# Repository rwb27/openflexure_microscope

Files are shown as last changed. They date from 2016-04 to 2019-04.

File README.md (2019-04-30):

# This repository has moved!
Active development continues on [GitLab.com](https://gitlab.com/openflexure/openflexure-microscope/) where you can find not only the up-to-date microscope designs, but also software and lots of other fun goodies.

# OpenFlexure Microscope
The OpenFlexure Microscope is a  3D printable microscope, including a precise mechanical stage to move the sample and focus the optics.  There are many different options for the optics, ranging from a webcam lens to a 100x, oil immersion objective.

An OpenFlexure Microscope in an incubator (courtesy Stephanie Reichelt and Dario Bressan at CRUK, Cambridge)

The trick of making a microscope out of a webcam has been around for a little while, and produces good results.  However, getting a nice mechanical stage to focus the microscope and move around on the sample is tricky.  This project is a 3D printable design that enables very fine (sub-micron) mechanical positioning of the sample and the lens, with surprisingly good mechanical stability.  It's discussed in various [media articles](https://github.com/rwb27/openflexure_microscope/wiki/Media-Articles) and a [paper in Review of Scientific Instruments](http://dx.doi.org/10.1063/1.4941068) (open access).

## Come join us!
Most of the development of this design has been done as part of various [research projects](http://www.bath.ac.uk/physics/contacts/academics/richard-bowman/index.html) - if you would like to join our research group at Bath, and you have funding or are interested in applying for it, do get in touch.  Check the University of Bath jobs site, or findaphd.com, to see if we are currently advertising any vacancies.  The team is bigger than Bath, though, and there are contibutors in Cambridge, Dar es Salaam, and beyond.

## Kits and License
This project is open-source and is released under the CERN open hardware license.  We are working on bring able to sell kits, and will update here once we have a good way of doing it,

## Printing it yourself
To build the microscope, go to [version 5.20 release](https://github.com/rwb27/openflexure_microscope/releases/tag/v5.20.0-b) and download the STL files and instructions.  Don't just print everything from the STL folder,
as there are a number of different configurations possible.  The [assembly instructions](http://rwb27.github.io/openflexure_microscope/docs/) contain instructions on what parts to print and how to build it.

If you've built one, let us know - add yourself to the [wiki page of builds](https://github.com/rwb27/openflexure_microscope/wiki/Assembly-Logs) or submit a [build report issue](https://github.com/rwb27/openflexure_microscope/issues/new?labels=build%20report).  This is a really helpful thing to do even if you don't suggest improvements or flag up problems.

## Instructions
The editable instructions are MarkDown format, in the [docs folder](./docs/), and [they can be viewed on github pages](http://rwb27.github.io/openflexure_microscope/docs/).

## Get Involved!
This project is open so that anyone can get involved, and you don't have to learn OpenSCAD to help (although that would be great).  Ways you can contribute include:

* Get involved in [discussions on gitter](https://gitter.im/OpenFlexure-Microscope/Lobby) 
* Share your microscope images (of both microscopes and what you've seen with them) in the [gallery](http://rwb27.github.io/openflexure_microscope/gallery/)
* [Raise an issue](https://github.com/rwb27/openflexure_microscope/issues) if you spot something that's wrong, or something that could be improved.  This includes the instructions/documentation.
* Suggest better text or images for the instructions.
* Improve the design of parts - even if you don't use OpenSCAD, STL files or descriptions of changes are helpful.
* Fork it, and make pull requests - again, documentation improvements are every bit as useful as revised OpenSCAD files.

Things in need of attention are currently described in [issues](https://github.com/rwb27/openflexure_microscope/issues) so have a look there if you'd like to work on something but aren't sure what.

## Related Repositories
Most of the Openflexure Microscope stuff lives on GitHub, under [my account](https://github.com/rwb27/).  Particularly useful ones are:
* The ["sangaboard" motor controller](https://github.com/rwb27/openflexure_nano_motor_controller/) based on an Arduino Nano + Darlington Pair ICs, developed collaboratively with [STICLab](http://www.sticlab.co.tz)
* The ["fergboard" motor controller](https://github.com/fr293/motor_board) by Fergus Riche
* An as-yet-quite-basic set of scripts that should become the [microscope software](https://github.com/rwb27/openflexure_microscope_software/)
* The higher precision, smaller range [block stage](https://github.com/rwb27/openflexure_block_stage)
* Some [characterisation scripts for analysing images of the USAF resolution test target](https://github.com/rwb27/usaf_analysis/)

## Compiling from source
If you want to print the current development version, you can compile the STL from the OpenSCAD files - but please still consult the documentation for quantities and tips on print settings, etc.  You can use GNU Make to generate all the STL files (just run ``make all`` in the root directory of the repository).  More instructions, including hints for Windows users, are available in [COMPILE.md](https://github.com/rwb27/openflexure_microscope/blob/master/COMPILE.md).

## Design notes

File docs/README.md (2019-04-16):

# The OpenFlexure Microscope: Assembly Instructions
The OpenFlexure Microscope is a 3D printable microscope, with a very precise mechanical translation stage.  It can be fitted with basic webcam-based optics, or more expensive optics based on a traditional microscope objective for higher image quality.  It can also be motorised.  These instructions will take you through how to assemble the microscope optical and mechanical parts.

## Printing the parts
Before we start, a note on printing - there are many possible versions of the microscope, so don't just print everything in the folder of STL files.  Currently, there's a readme document in the ``builds`` folder explaining how to select your versions.  Please do consult it before printing.  Also note that the parts are designed to print without support material on most RepRap type printers.  If you use support material, the parts will be difficult to clean up, and may well be damaged in the process - particularly the delicate main body.

## Contents
Assembly is broken up into several steps:
* [Obtaining non-printed parts](./0_bill_of_materials.md)
* [Printing parts](./0_printing.md)
* [Assembling the actuators](./1_actuator_assembly.md) deals with the mechanism for moving the stage.
* The optics module comes next, either the [basic optics module](./2a_basic_optics_module.md) or the [high resolution optics module](./2b_high_resolution_optics_module.md) depending on your needs.
* [Illumination](./3_illumination.md) covers attaching the condenser.
* [Sample clips and wiring](./4_clips_and_wiring.md) completes the microscope.
* [Motors](./5_motors.md) can be added for automatic control.

Happy building!

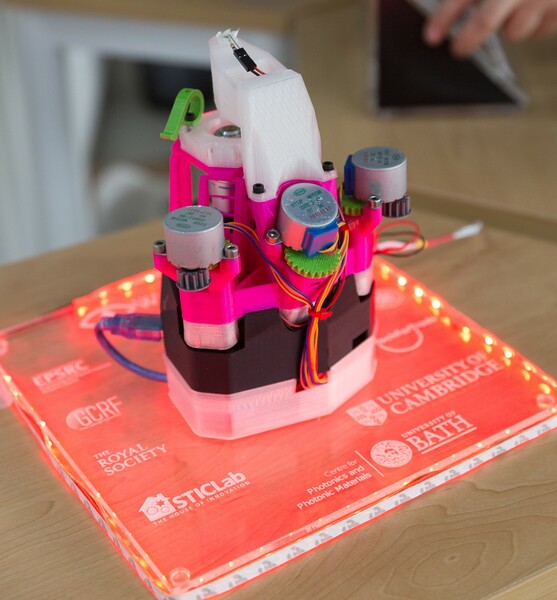
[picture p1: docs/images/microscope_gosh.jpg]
An assembled OpenFlexure Microscope, courtesy of GOSH 2018


## About the microscope
The OpenFlexure microscope is a customisable optical microscope, using either very cheap webcam optics or lab quality, RMS threaded microscope objectives.  It uses an inverted geometry, and has a high quality mechanical stage which can be motorised using low cost geared stepper motors.

The original paper describing this work is available open-access from [Review of Scientific Instruments](http://dx.doi.org/10.1063/1.4941068) and you can read various [media articles](https://github.com/rwb27/openflexure_microscope/wiki/Media-Articles) about it for a more user-friendly introduction.

Optomechanics is a crucial part of any microscope; when working at high magnification, it is absolutely crucial to keep the sample steady and to be able to bring it into focus precisely.  Accurate motion control is extremely difficult using printed mechanical parts, as good linear motion typically requires tight tolerances and a smooth surface finish.  This design for a 3D printed microscope stage uses plastic flexures, meaning its motion is free from friction and vibration.  It achieves steps well below 100nm when driven with miniature stepper motors, and is stable to within a few microns over several days.

This design aims to minimise both the amount of post-print assembly required, and the number of non-printed parts required - partly to make it as easy as possible to print, and partly to maximise stability; most of the microscope (including all the parts with flexures) prints as a single piece.  The majority of the expense is in the Raspberry Pi and its camera module; the design requires only around 200g of plastic and a few nuts, bolts and other parts.  The optics module (containing the camera and lens) can be easily swapped out or modified, for example to change the magnification/resolution by using a microscope objective, or adding a filter cube for fluorescence.

## Acknowledgements
This design has largely come out of academic research projects, and we would like to acknowledge financial support from:
* The [Engineering and Physical Sciences Research Council](http://epsrc.ukri.org/) (grants EP/P029426/1, EP/R013969/1)
* The Royal Society
* The Royal Commission for the Exhibition of 1851
* Queens' College, Cambridge

The lead developer started this project while at the University of Cambridge, and continues to work on it at the University of Bath, UK.

## Contributors
* Richard Bowman <r.w.bowman@bath.ac.uk> (University of Bath)
* Julian Stirling (University of Bath)
* Grace Anyelwisye Mwakajinga (STICLab)
* Valerian Sanga (STICLab)
* Qixing Meng (University of Bath)

This design is (c) the contributors, released under the CERN open hardware license.

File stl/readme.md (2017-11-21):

# OpenFlexure Microscope STL Files
tl;dr **don't print these files if you want a microscope!** You should either go to the [documentation](../docs/) or the automatically built files in [builds](../builds/) (see the readme there for details of how to pick the right files to print).  You can also clone the repository and build it yourself if you have ``make`` and ``openscad``.  Bear in mind that these STL files might not perfectly match the instructions, as they get improved faster than the photos can be re-taken!

This folder is for STL files that have been compiled outside of the usual build process.  It's possible I should have excluded these from the repo, as they are build products - but it's often handy to have them here.  I will probably get rid of this folder in the future.  *Please don't just print this folder* as it does not add up to a full microscope!

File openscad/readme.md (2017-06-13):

OpenFlexure Microscope: OpenSCAD Source
=======================================

This folder contains the source code that generates the STL files that you print to produce the microscope.  The relationship between the source files and the STL files is not yet 1:1, though I'm gradually working on that.  Most of the SCAD files produce a corresponding STL, but there are a few key support files that don't:

* ``microscope_parameters.scad`` defines most of the important variables (parameters) used in the design, for example the size of the microscope, whether or not it has motor lugs, etc. etc. - this is the file you are most likely to need to modify, for example to produce a microscope with particular settings.
* ``utilities.scad`` contains lots of handy functions I've coded along the way.  It's a slightly random assortment, but they are used in most of the other files and save a fair bit of typing.
* ``dovetail.scad`` defines the dovetail clips used to hold the optics module and the condenser.
* ``compact_nut_seat.scad`` defines the actuator column (the bit that holds the screw, nut and elastic band).  This is one of the most useful files for other projects - e.g. the OpenFlexure Block Stage uses it extensively.
* ``logo.scad`` is used to stamp the WaterScope logo on the microscope

Then for the main parts of the microscope:
* ``main_body.scad`` defines the main body.  This is by far the biggest file as you might expect.
* ``feet.scad`` produces the three front feet (two tilted and one untilted)
* ``gears.scad`` makes 3 gears for the actuators.
* ``illumination_and_rear_foot.scad`` produces the illumination column, which is combined with the back foot.  It's now in three pieces, for easier printing and to allow some adjustment of the condenser position.
* ``optics.scad`` defines, amongst other things, the optics module (the mount for the camera and objective).  This has a number of commented-out sections that must be uncommented depending on what you want to produce.  In particular, you must choose manually between an RMS objective and using a simpler lens.  You must also uncomment the correct line at the top of the file for the camera - the design will work with several camera modules defined in the ``cameras`` folder.
* ``sample_clip_2.scad`` produces clips to hold microscope slides onto the microscope stage.  This is now set to print two, and produces an STL file that is print-ready (i.e. the clips are on their side).
* ``sample_riser_2.scad`` makes a 10mm thick platform for a microscope slide.  You may need to use comments at the bottom of the file to print either the sample riser or the clip that holds the slide on.  A small spring is required to put the clip in the right place.
* ``small_gear.scad`` makes the gear you fit on a motor if you want to motorise the microscope.  NB it only makes one gear.

There are some that make tools too:
* ``actuator_assembly_tools.scad`` defines the tool for inserting elastic bands, and the tooll for pushing nuts into nut slots.  NB there is a new double-ended band tool defined at the bottom of the file, you'll need to use the comments to either produce this or the old-style one.
* ``tube_lens_tool.scad`` produces a ring of plastic, suitable for pushing the tube lens into its push-fit mount without damaging it.
* ``condenser_lens_tool.scad`` produces a ring of plastic, suitable for pushing the condenser lens into its push-fit mount without damaging it.
* ``lens_removal_tools.scad`` produces the tools needed to remove the lens from the Raspberry Pi camera module.  NB the lens removal tool is now superseded by the injection-moulded tool supplied by Raspberry Pi with each camera, but the board holder still helps to avoid damaging the flex.

Other files:
* ``baseplate.scad`` and ``baseplate_minimal.scad`` generate a baseplate, suitable for gluing onto some foam, if you want to mount the microscope in a box.  It's still work in progress...
* ``illustrations/`` contains various SCAD files that aim to create the illustrations needed for the instructions.  Very much work in progress, it's nowhere near finished.

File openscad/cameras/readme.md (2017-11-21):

# OpenFlexure Microscope: Camera Mounts

Curently, the OpenFlexure microscope will work with:
* Raspberry Pi camera module v2 (v1 is possible but deprecated, as it's discontinued)
* Logitech C270 webcam (you need to dissassemble it and remove the microphone)
* USB camera with standard M12 lens (WaterScope source these from China)

The way this is done is that ``optics.scad`` includes ``camera.scad``, which defines the important functions/modules for interfacing with the camera.  These are then used to make the optics module accordingly.  The variable ``camera`` (defined in ``microscope_parameters.scad`` or on the command line). Those functions are:

* ``camera_mount_height()``: a function that returns the height of the mount (above this height, we will make the optics module - this is the distance below the ground plane of the microscope body that the camera PCB will sit).
* ``camera_sensor_height()``: the distance above the PCB that the camera sensor sits - it's used in the optics module to calculate the position of the lens.
* ``camera_mount()``: a module that builds a mount for the camera.  If you print this on its own, it should create a flat(ish) structure, ``camera_mount_height()`` high, that fits onto the camera, with the sensor centred on the origin.

There are 3 options for the camera:
* picamera_2: mount for Raspberry Pi camera v2
* logitech_c270: for Logitech C270 webcam
* m12: this replaces the M12 lens holder on a USB camera.  It should work with most cameras that have an M12 lens held onto the board by two screws.

The ``picamera_2.scad`` file also defines the cover for the bottom of the camera PCB and the tools for removing the lens (see below).  There's no cover for the Logitech PCB, I often use a bit of extra-large heatshrink (it's thinner than a printed cover would be, which is helpful).

Previous versions of the microscope had push-fit mounts for the Pi camera v1 and v2, but it was very easy to break the delicate flex on the camera module when fitting these, so they are now removed.  See previous versions if you need those.

## Pi Camera v2 accessories
The extra files ``picamera_2_<thing>.scad`` generate the board gripper and lens gripper that can be used to remove the lens of the Raspberry Pi camera v2, and a little cover for the bottom of the PCB to protect it from shorts, etc.  The lens gripper is now obsolete as a much better, injection-moulded gripper is now supplied in the pi camera box.  The gripper for the PCB is still useful as it protects the flex cable from damage while you remove the lens.

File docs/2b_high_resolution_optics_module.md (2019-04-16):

# High resolution optics module
To get lab quality images from your microscope, you need to use more sophisticated optics than a webcam lens.  This optics module uses an RMS threaded microscope objective, with a tube length correction lens, to take very high quality images.

# Requirements
You will need the parts shown in the picture below:

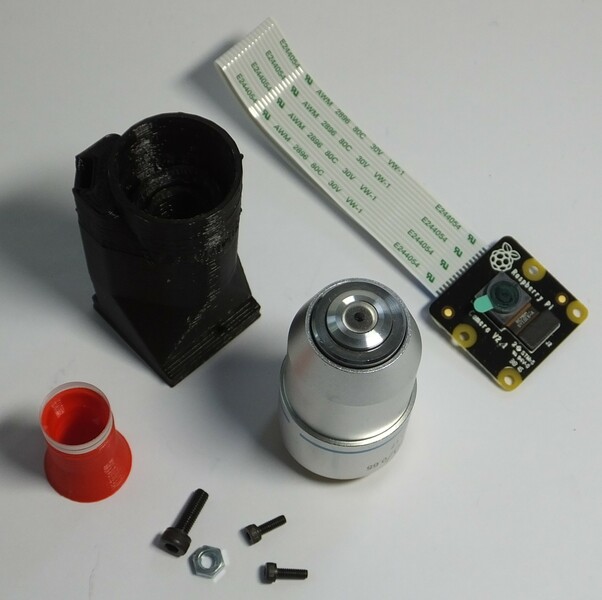
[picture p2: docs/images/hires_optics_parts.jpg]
Parts required for this step


## Parts
*   1 [RMS optics module casing](./parts/hires_optics_casing)
*   1 [Raspbery Pi camera module](./parts/electronics/raspberry_pi_camera.md)  (ideally v2, though v1 should also work)
*   1 [M3 steel nut](./parts/fixings/m3_steel_nut.md)
*   1 [M3x10mm cap head screw](./parts/m3x10mm_cap_head)
*   2 [M2x6mm cap head screws](./parts/m2x6mm_cap_head)
*   1 [12.7mm diameter, 50mm focal length achromatic lens](./parts/d13_f50_achromat)
*   1 RMS threaded microscope objective

## Tools
*   1 [Tube lens insertion tool](./parts/tube_lens_insertion_tool)
*   1 2.5mm hex key
*   1 1.5mm hex key
*   1 scalpel or craft knife (optional)
*   1 [Tool for removing the lens](./parts/camera_lens_removal_tools)

# Assembly Instructions
## Step 1
First, get the necessary tools and parts: the optics module plastic part, the Raspberry Pi camera module, the tools for removing the camera lens, two M2 screws to secure the camera, the tube lens, and the objective.  Depending on print quality, you might also need a sharp craft knife.
 
NB the lens removal tools, board gripper, and optics module are all specific to the camera you're using.  This version of the instructions is for version 2 of the camera board, version 1 of the Rasbperry Pi camera module will also work, but you will need to remove the lens with pliers or tweezers instead.  Version 2 of the camera module ships with a lens removal tool included, which is a white disc of plastic with a hole in the centre.  This is better than the printed lens removal tool, if it's available.

## Step 2
Before assembling the parts into the holder, make sure it's free from dust by blowing some air through it, and check there are no strings of plastic in the central hole through the mount - an example with strings of plastic is shown in the picture.  Use a craft knife to remove these strings, and blow out any debris that remains inside the optics module.

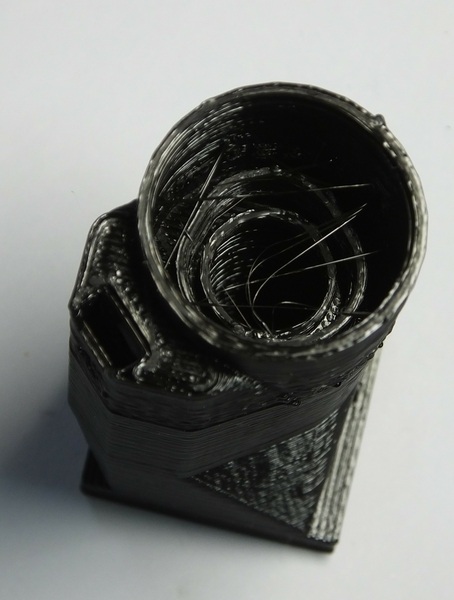
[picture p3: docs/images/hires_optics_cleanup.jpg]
Strings of plastic in the optics module


## Step 3
Slide the M3 nut into the plastic holder, and screw the M3 screw into it as shown.  This will mount the optics module into the microscope.

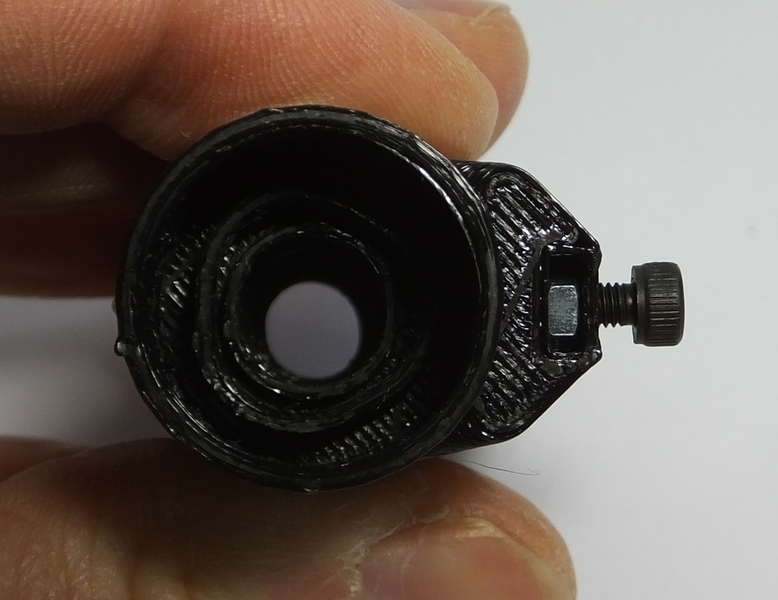
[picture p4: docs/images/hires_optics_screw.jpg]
Adding the mounting screw and nut


## Step 4
Next, put the lens into the push-fit holder.  Start by placing the tube lens insertion tool on a table, with the larger end down.  Then, put the lens on the tool (shown in red below), with the more convex side facing down.  Next, carefully line up the optics module casing with the lens, and push it down on top of the lens.  This might take a little force, I use the heel of my hand.  The glass lens is harder than the plastic so is unlikely to crack, but try to avoid too much sideways motion, as this can scratch the surface of the lens.

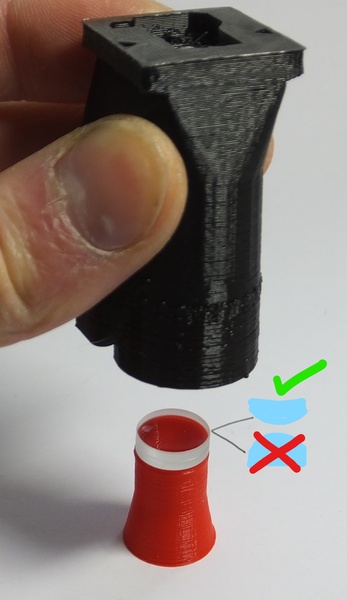
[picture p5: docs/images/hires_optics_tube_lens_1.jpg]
The lens ready to be inserted

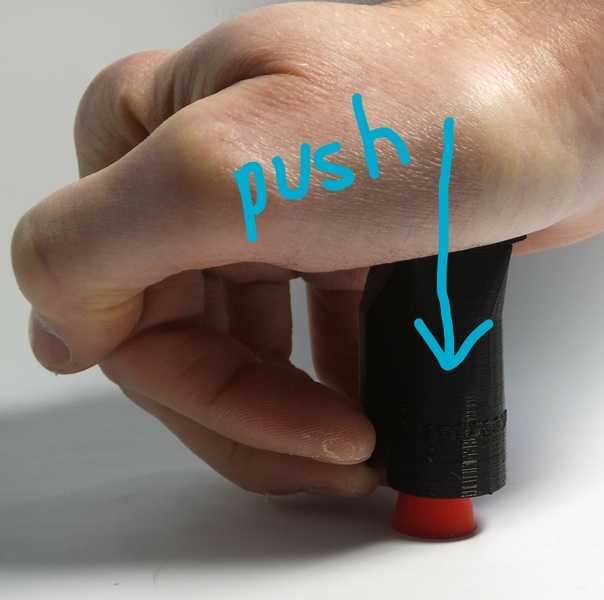
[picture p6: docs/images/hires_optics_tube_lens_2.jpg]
Inserting the lens

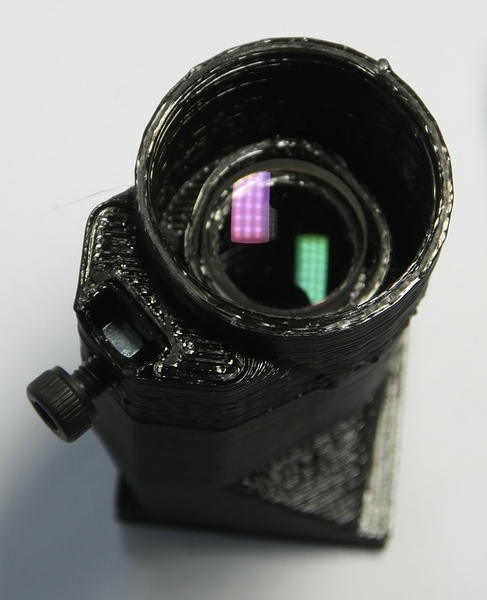
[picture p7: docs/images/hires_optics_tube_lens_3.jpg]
The tube lens, fitted into the optics module


## Step 5
Screw the objective into the plastic casing.  The printed thread is not hugely strong, and may not have printed very precisely - the means it might be a little loose or a little tight, and you need to be very careful to screw the objective in straight in order to avoid cross-threading.

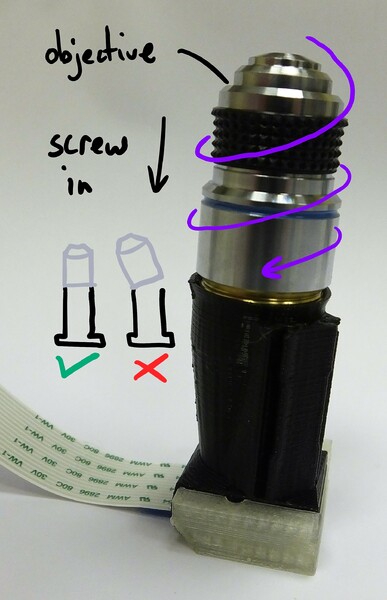
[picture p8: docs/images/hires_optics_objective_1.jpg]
Screw the objective in to the mount - be careful to keep it straight!

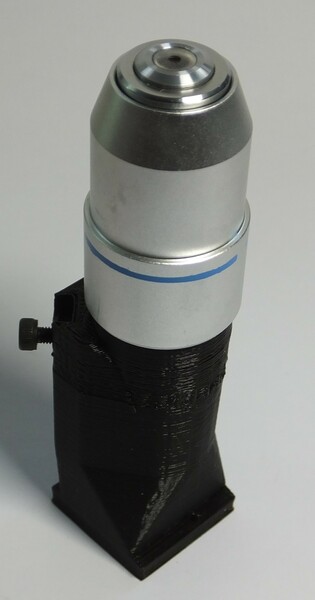
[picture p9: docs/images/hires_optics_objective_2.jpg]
The objective, in place in the optics module


## Step 6
We need to remove the lens from the camera.  To do this, you need the two plastic tools (the board gripper and the lens remover) as well as the camera module.  It's best to make sure you have completed the steps up to this point before removing the lens, to minimise the amount of time the sensor is exposed to air and dust.

> **WARNING!** The camera board is static sensitive.  Take the usual anti-static precautions (ideally use an anti-static wristband connected to ground, but at the very least make sure you touch an earthed object, such as a metal pipe, before working on the camera module.

## Step 7
Remove the protective film from the camera lens.

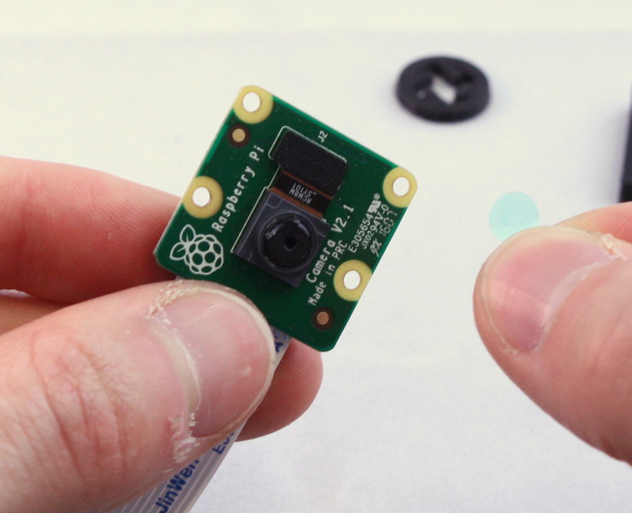
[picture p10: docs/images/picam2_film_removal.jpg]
Removing the protective film from the lens


## Step 8
There is a small ribbon cable connecting the camera to the PCB that is very easy to break.  There is a square plastic jig that fits over the camera and PCB (the "camera board gripper"), which stops the camera twisting and damaging the ribbon cable.  Fit this over the camera as shown.  Note that the part for v2 of the camera board will sort-of fit v1, but you need to be a little more careful as it's not a perfect fit.

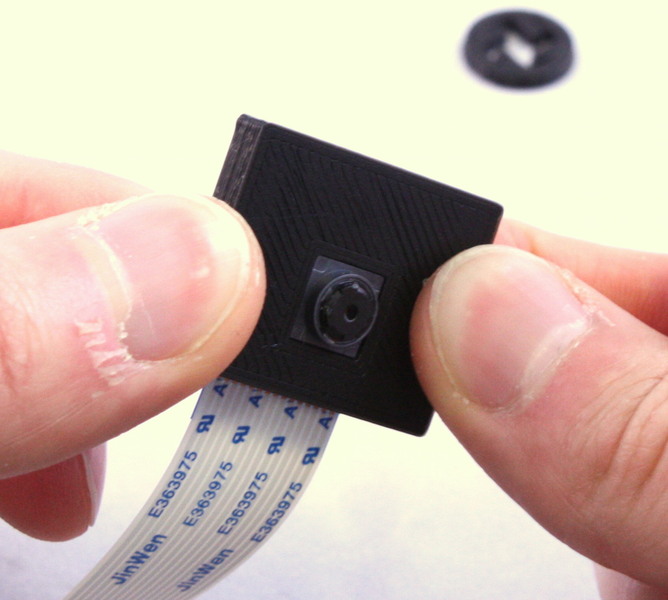
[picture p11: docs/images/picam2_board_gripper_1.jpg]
The board gripper

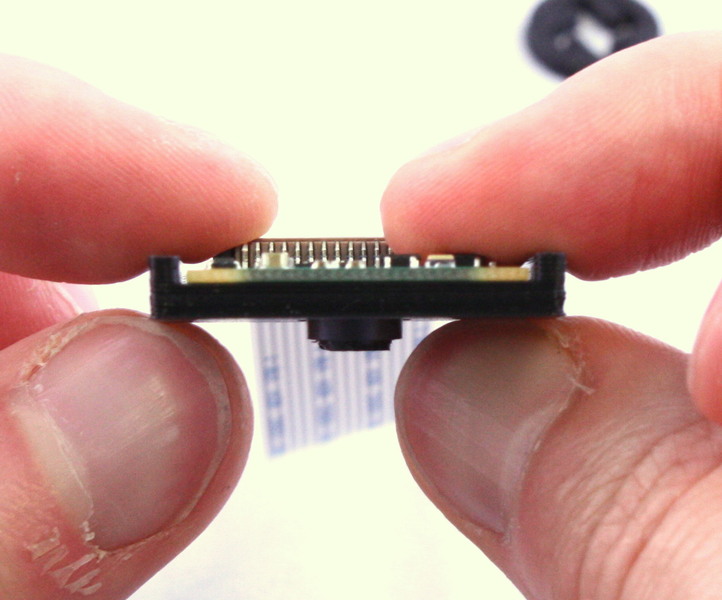
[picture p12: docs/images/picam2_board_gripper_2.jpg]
Gripping the camera to prevent damage to the ribbon cable


## Step 9
Next, unscrew the lens from the camera module.  Use the plastic tool to grip the lens module.  This is a small circular part with four prongs that fits over the lens of the camera board (version 2 only) as shown.  To remove the lens, push the removal tool onto the lens (just the top part, with the little plastic flanges) and turn anticlockwise to remove it.
 
The printed tool only works if the prongs are pointing anticlockwise, so make sure it's the right way round.  The plastic tool supplied with the camera module is better, and only fits one way up.  It's important to use the board gripper to hold the camera chip in place and prevent damage to the delicate ribbon cable.  After you've removed the lens, check that the little black (or orange) ribbon cable connecting the camera module to the PCB is still connected - pop it back in by pushing it with a finger if needed.

Once you've removed the lens, be sure to place the camera face down on the desk, or put a piece of tape over the square black lens holder; this will help stop dust settling on the sensor, which is extremely hard to clean.

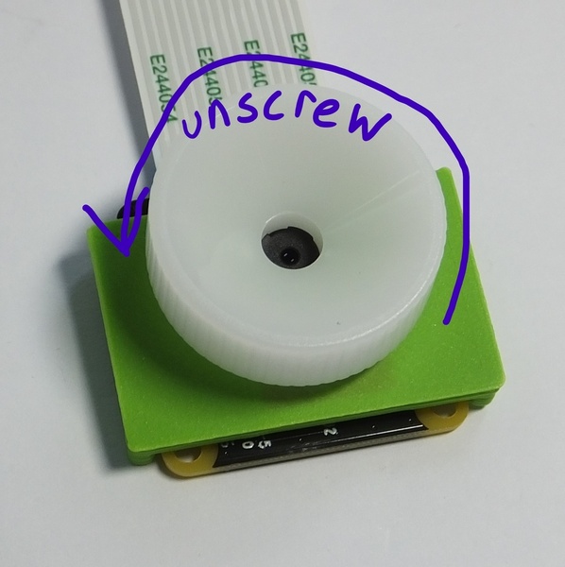
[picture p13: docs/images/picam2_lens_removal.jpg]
Lens removal


## Step 10
Fit the camera module on to the bottom of the plastic housing, and secure it in place with the two M2 screws.

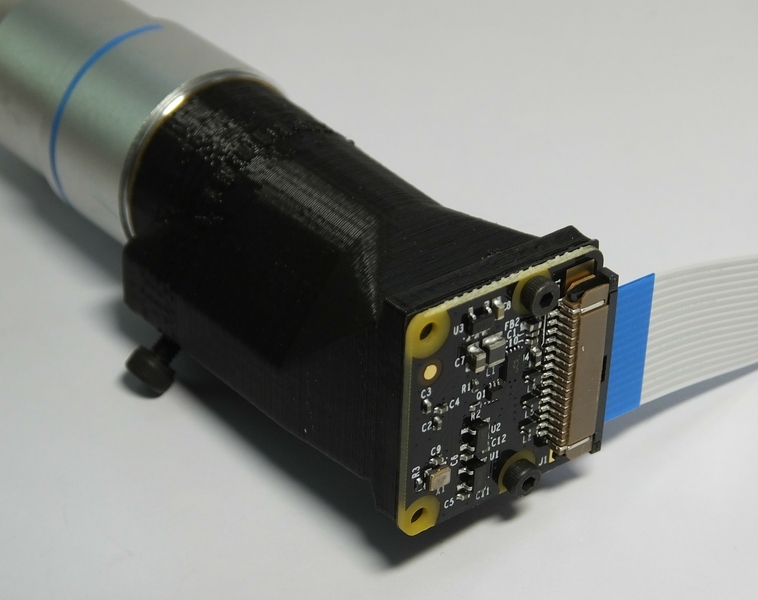
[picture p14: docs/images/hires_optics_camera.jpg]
The camera, held in place by two M2 screws


## Step 11
Well done - you have assembled the optics module.

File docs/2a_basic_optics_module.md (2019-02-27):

# Basic optics module
The simplest option for the microscope optics is to use a webcam lens.  This is an old photographers' trick, where a wide angle lens is turned backwards and used as a macro lens, so the side that would have pointed at the camera sensor now points at the sample.  Because webcams have very small pixels, using a webcam in reverse makes quite a good microscope objective.  This version of the optics module turns the Raspberry Pi camera into a microscope with a field of view about 400um across and a resolution of around 2um.

# Requirements
You will need the parts shown in the picture below:

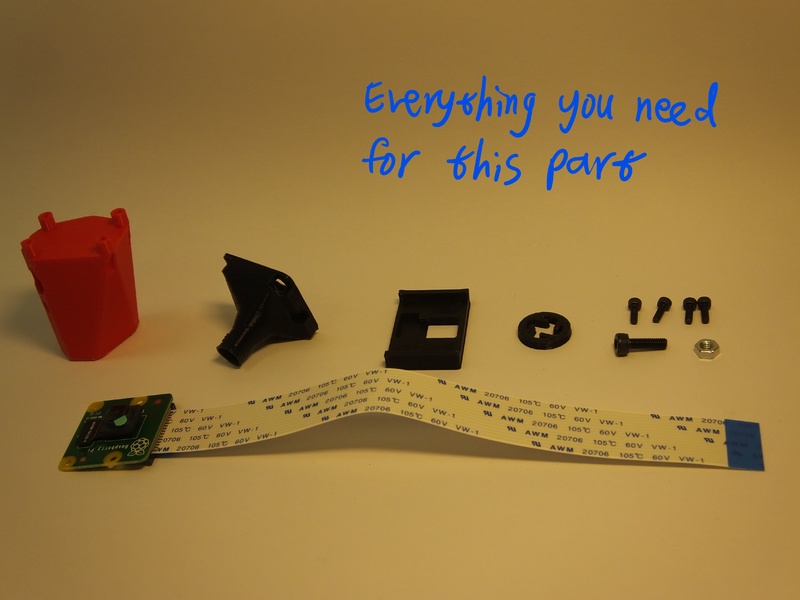
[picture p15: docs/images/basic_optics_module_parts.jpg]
Parts required for this step


## Parts
*   1 [Camera platform](./parts/camera_platform)
*   1 [Lens extension tube](./parts/lens_spacer)
*   1 Raspberry Pi camera module (ideally v2, though v1 should also work) - you could substitute a 6-LED webcam for an even lower-cost solution.
*   1 [M3 steel nut](./parts/m3_nut)
*   1 [M3x10mm cap head screw](./parts/m3x10mm_cap_head)
*   4 [M2x6mm cap head screws](./parts/m2x6mm_cap_head)

## Tools
*   1 2.5mm hex key
*   1 1.5mm hex key
*   1 scalpel or craft knife (optional)
*   1 [Tool for removing the lens](./parts/camera_lens_removal_tools)

# Assembly Instructions
## Step 1
First, get the necessary tools and parts: the optics module plastic parts (the lens spacer and the camera platform), the Raspberry Pi camera module, the tools for removing the camera lens, two M2 screws to secure the camera.  Depending on print quality, you might also need a sharp craft knife or some tape.
 
NB the lens removal tools, board gripper, and optics module are all specific to the camera you're using.  This version of the instructions is for version 2 of the camera board, version 1 of the Rasbperry Pi camera module will also work, but you will need to remove the lens with pliers or tweezers instead.  Version 2 of the camera module ships with a lens removal tool included, which is a white disc of plastic with a hole in the centre.  This is better than the printed lens removal tool, if it's available.

If you are using the 6-LED USB webcam (available for around £3 from eBay or AliExpress) you will need to skip some of these steps and also disassemble the plastic casing to extract the circuit board for the camera.  You can simply unscrew the webcam lens and tape or glue it upside down onto the holder, which is fixed onto the circuit board.  There is a camera platform STL for the 6-LED camera in the build, substitute this for the Raspberry Pi camera platform part.

## Step 2
We need to remove the lens from the camera.  To do this, you need the two plastic tools (the board gripper and the lens remover) as well as the camera module.  It's best to make sure you have completed the steps up to this point before removing the lens, to minimise the amount of time the sensor is exposed to air and dust.

> **WARNING!** The camera board is static sensitive.  Take the usual anti-static precautions (ideally use an anti-static wristband connected to ground, but at the very least make sure you touch an earthed object, such as a metal pipe, before working on the camera module.

## Step 3
Remove the protective film from the camera lens.

Removing the protective film from the lens

## Step 4
There is a small ribbon cable connecting the camera to the PCB that is very easy to break.  There is a square plastic jig that fits over the camera and PCB (the "camera board gripper"), which stops the camera twisting and damaging the ribbon cable.  Fit this over the camera as shown.  Note that the part for v2 of the camera board will sort-of fit v1, but you need to be a little more careful as it's not a perfect fit.

The board gripper
Gripping the camera to prevent damage to the ribbon cable

## Step 5
Next, unscrew the lens from the camera module.  Use the plastic tool to grip the lens module.  This is a small circular part with four prongs that fits over the lens of the camera board (version 2 only) as shown.  To remove the lens, push the removal tool onto the lens (just the top part, with the little plastic flanges) and turn anticlockwise to remove it.
 
The printed tool only works if the prongs are pointing anticlockwise, so make sure it's the right way round.  It's important to use the board gripper to hold the camera chip in place and prevent damage to the delicate ribbon cable.  After you've removed the lens, check that the little black or orange ribbon cable connecting the camera module (the black square of plastic from which you unscrewed the lens) to the PCB is still connected - pop it back in by pushing it with a finger if needed.

Once you've removed the lens, be sure to place the camera face down on the desk, or put a piece of tape over the square black lens holder; this will help stop dust settling on the sensor, which is extremely hard to clean.

Lens removal

## Step 6
Before assembling the parts into the holder, make sure it's free from dust by blowing some air through it, and check there are no strings of plastic in the central hole through the mount.

## Step 7
Next, put the lens into the plastic extension tube.  The lens should go in with the side that was next to the camera sensor on top, and the side that was facing outwards (the one with a small hole in the black plastic) facing into the extension tube.  This should just push-fit, but may take a small amount of force, or  require a layer of tape wrapped around the lens to make it fit tightly (depending on your printer).  If you wrap tape around the lens, trim off any tape that protrudes above the lens with a scalpel or sharp craft knife.

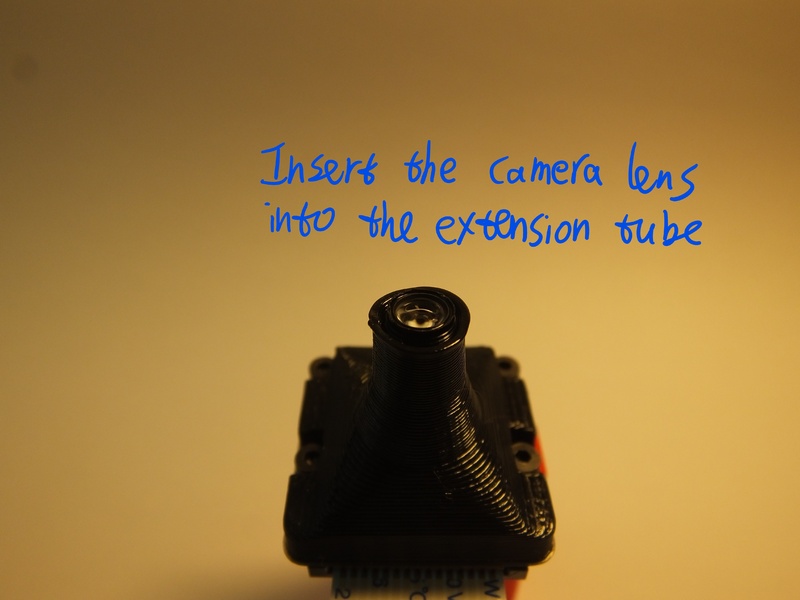
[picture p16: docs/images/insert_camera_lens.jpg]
The lens in the extension tube

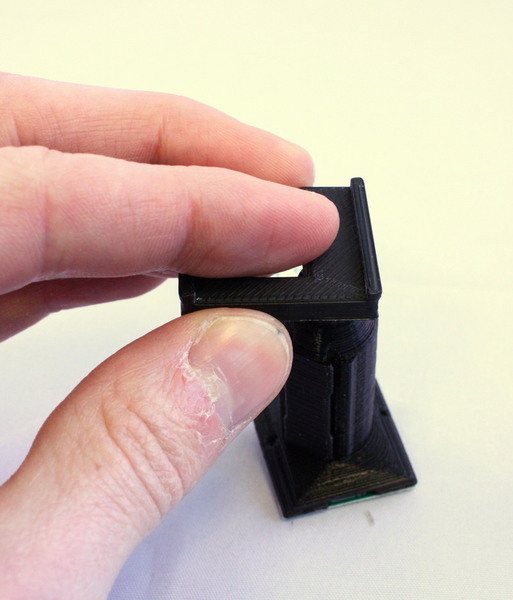
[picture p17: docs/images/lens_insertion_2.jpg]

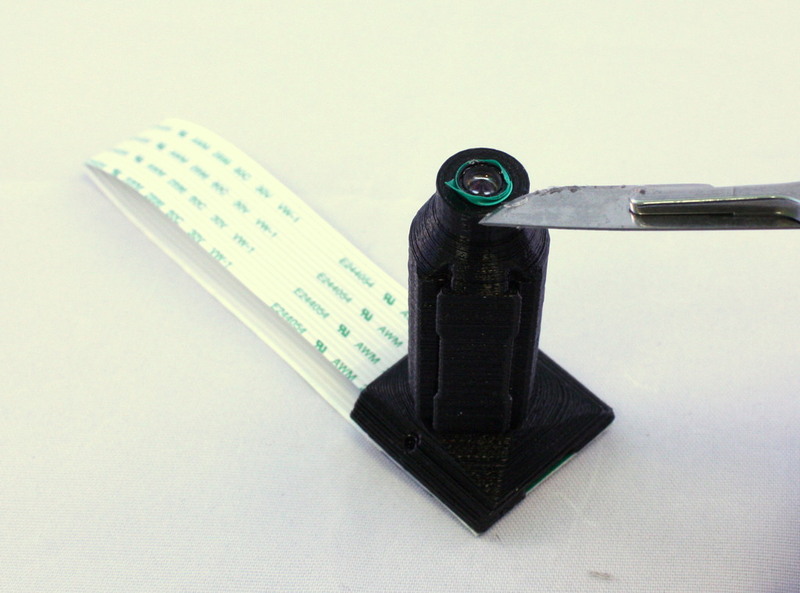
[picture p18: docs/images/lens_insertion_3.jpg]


## Step 8
Fit the extension tube onto the camera board, then put the camera board and extension tube onto the camera platform.  Secure it in place with two M2 screws, which go through the extension tube and the camera board, and into the platform.  You can use two more M2 screws if available to make the joint stronger.

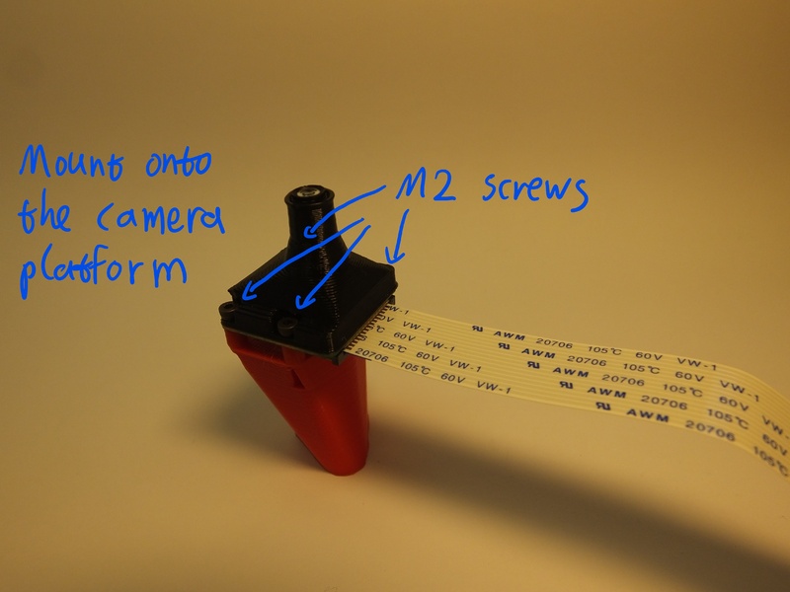
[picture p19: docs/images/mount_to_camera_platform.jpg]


## Step 9
Slide a nut into the nut trap on the side of the camera platform.  This probably doesn't need a tool, but you could use a 2.5mm hex key to push it in.

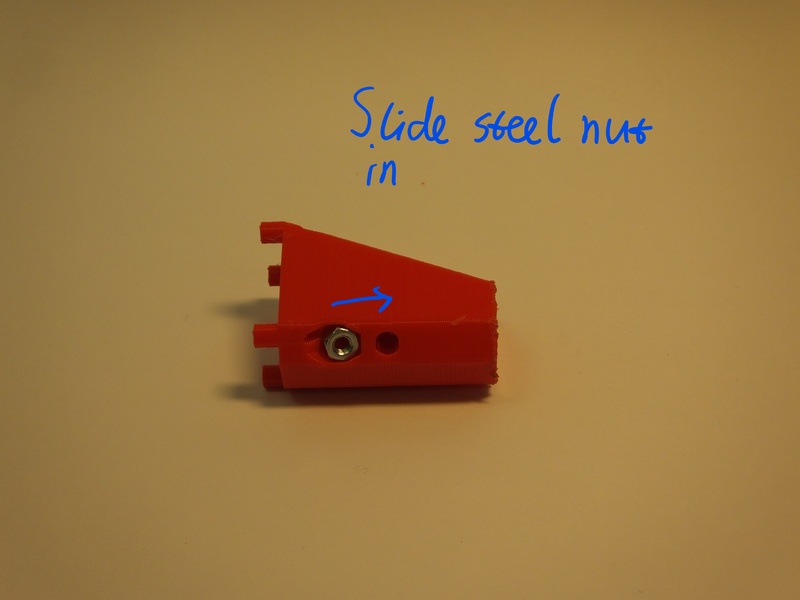
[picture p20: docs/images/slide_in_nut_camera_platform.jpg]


## Step 10
Screw the M3 screw into the nut, so that it sticks out the side of the camera platform.
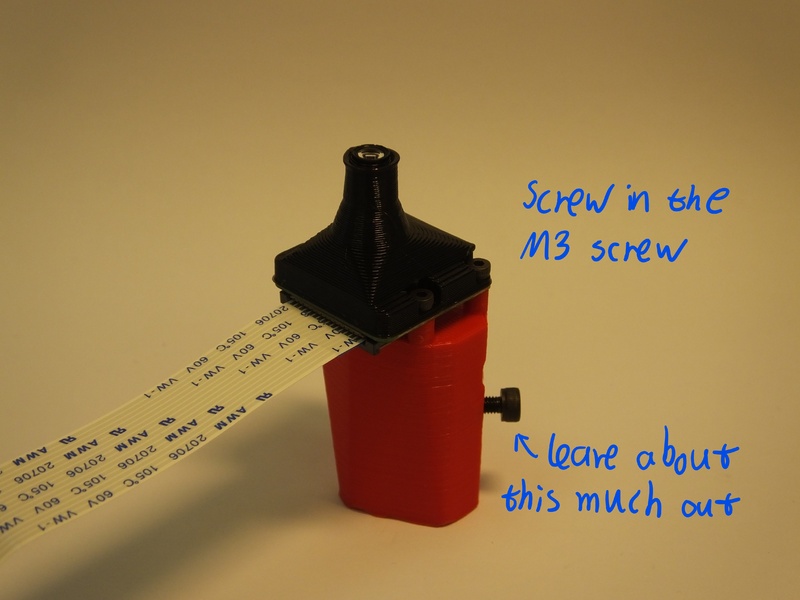
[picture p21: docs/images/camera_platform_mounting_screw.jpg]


## Step 11
Well done - you have assembled the optics module.

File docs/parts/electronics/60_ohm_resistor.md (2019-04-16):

# 60 Ohm resistor

## Details
*   **Supplier:** Farnell Element14
*   **Supplier's part number:** 1565328
*   **Manufacturer's part number:** MFR3-68RFC

This resistor allows the LED to be run from a 5V GPIO pin on the Raspberry Pi.  If you use a different LED, you may need a different resistor.  Note the maximum current you can draw from the Pi is not huge.

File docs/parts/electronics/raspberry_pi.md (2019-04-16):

# Raspberry Pi
Any model will do!  NB if you buy a Pi Zero, only the Zero+ has a camera connector, and even that needs a special lead.  Of course, if you're using a camera that's not the Raspberry Pi camera module, you can use whatever USB-compatible device you like.  Bear in mind that the holes in the microscope stand are designed for a Model B, so Model A or Zero won't fit correctly.

The Raspberry Pi will need a suitable 5v power supply, an SD card, and most likely a keyboard, monitor, and mouse to function correctly.

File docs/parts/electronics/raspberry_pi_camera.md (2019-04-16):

# Raspberry Pi Camera Module
We use almost exclusively the v2 camera module, which has a better sensor and a better lens.  The design should also work with v1, though removing the lens will be considerably harder.

Newer camera modules come with an included plastic tool for removing the lens - this is much better than the printed tool and should definitely be used in preference.

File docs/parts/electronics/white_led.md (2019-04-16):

# White LED

## Details
*   **Supplier:** RS Electronics
*   **Supplier's part number:** 713-3983
*   **Manufacturer's part number:** NSPL500DS

The white LED is for illumination.  Exact specifications are unimportant, but this is the one I use - it is the "warmest" white I could find, as this means the wavelength range is closer to a filament bulb.  5mm diameter is what I've designed for, but there's no reason you couldn't tweak the illumination arm to use a 3mm LED.

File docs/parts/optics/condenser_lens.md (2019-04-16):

# Condenser Lens

## Details
*   **Focal length:** 5mm
*   **Outer diameter:** 12.7mm
*   **Material:** PMMA

The illumination needs a condenser lens, and so far I have generally sourced these in bulk from China.  They are designed for collimating LEDs, and don't produce a beautiful image, but they are adequate for our purposes.  Searching AliExpress for 5mm and 13mm usually brings up the right thing.

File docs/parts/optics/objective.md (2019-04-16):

# Microscope objective
## Details
*   **Tube length:** 160mm
*   **Correction:** Plan
*   **Magnification:** 4x-100x
*   **Suppliers:** Comar Optics, ThorLabs, Olympus, Nikon, Zeiss, Sunlight Optical via AliExpress

The microscope should accept most RMS-threaded objective lenses, and depending on whether you use the sample riser it will use either 35mm or 45mm parfocal distance.  These objectives can typically be scavenged from old equipment, or obtained very cheaply on AliExpress.  We recommend going for Plan or Semi-Plan corrected lenses at 40x, and definitely Plan corrected or better at 100x.

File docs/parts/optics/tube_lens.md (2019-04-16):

# Tube lens
## Details
*   **Focal length:** 50mm
*   **Outer diameter:** 12.7mm
*   **Material:** glass
*   **Lens type:** cemented achromatic doublet
*   **Supplier:** ThorLabs
*   **Supplier part number:** AC127-050-A

The microscope is designed to use finite-conjugate microscope objectives.  However, it is necessary to shorten the distance between the objective and the sensor by inserting a lens in the intervening space.  This is **not** placed one focal length from the camera (as it would be in an infinity-corrected design) and so isn't really a tube lens - think of it as a "tube length correction lens".

These lenses can be conveniently sourced form ThorLabs, or less conveniently from AliExpress at lower cost.

The tube lens is only required if you are using an RMS microscope objective, i.e. in the high resolution version of the microscope.

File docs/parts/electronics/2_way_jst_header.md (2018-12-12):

# Jumper wires with female header pin connectors
Jumper wires with female header pin connectors

## Details
*   **Material units:** NONE

# Manufacturing Instructions
## Step
You need wires to connect the LED to the 5V power supply from the Raspberry Pi.  If you've bought a kit, it will be supplied with a ready-made lead that has the LED at one end and the header connector at the other end.  My preferred DIY option is two cores from a ribbon cable, soldered to the LED and resistor at one end and with a crimped-on connector at the other.  If you want a no-soldering solution, four female-female jumpers allow you to connect everything (using a cut-off leg of the resistor to join two of them together).

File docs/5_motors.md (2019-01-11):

# Motor assembly
The OpenFlexure Microscope can be motorised, to allow you to run automated experiments.  In order to do this, you will need to fit stepper motors to the X, Y, and Z axes.

# Requirements
You will need the parts shown in the picture below:

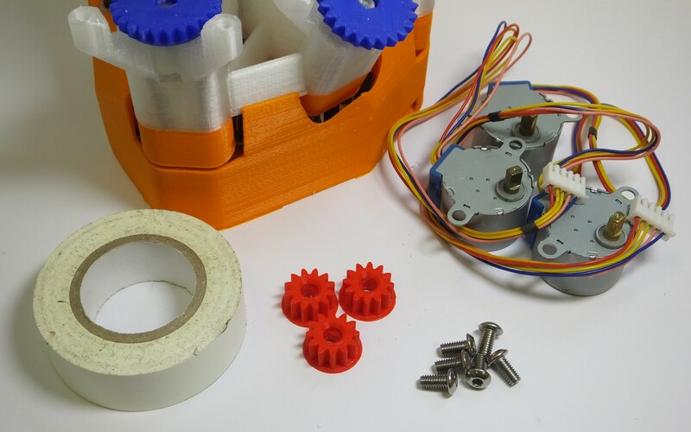
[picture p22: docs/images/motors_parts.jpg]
Parts required for this step


## Parts
*   1 Microscope, with actuators already assembled
*   3 Small printed gears
*   3 28BYJ-48 micro geared stepper motors
*   6 M4x6mm button head screws
*   1 Motor board case
*   1 Motor driver board
*   1 Short mini USB lead
*   2 Small cable ties

## Tools
*   1 2.5mm hex key
*   3cm insulating tape

# Assembly Instructions
## Step 1
First, fit the gears onto the motors.  The gears are printed with a circular bottom - place them on the table, circular side down.  They should be a tight fit onto the motor shaft - if they are not, place some insulating tape, sticky side up, on top of the gear as shown.

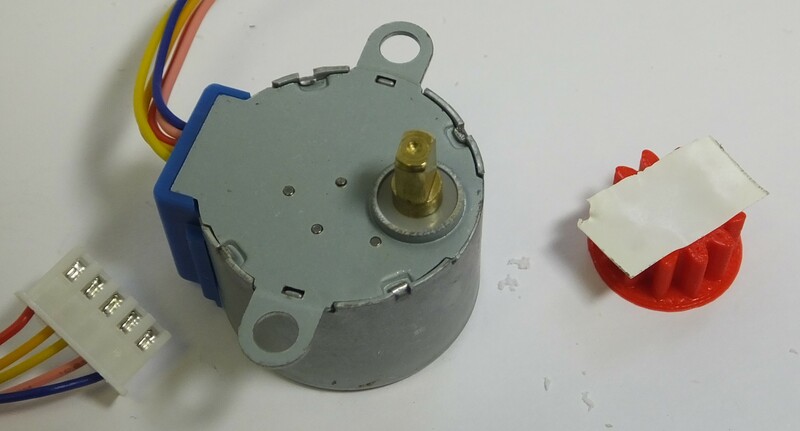
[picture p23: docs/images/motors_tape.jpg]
A motor and gear, ready for assembly


## Step 2
Now, fit the gear (and tape) onto the motor shaft - with the gear on the table, press the shaft into the hole.  NB you need to line the flat sides of the shaft up with the hole - it is not circular.

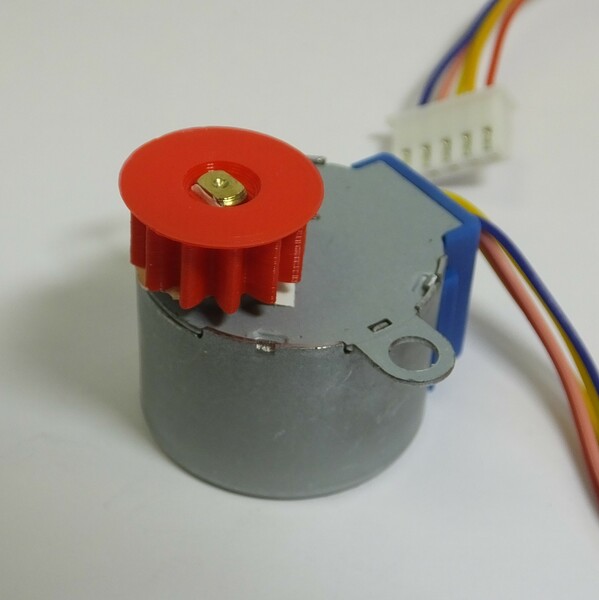
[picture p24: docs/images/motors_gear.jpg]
A motor with the gear on its shaft


## Step 3
Repeat steps 1 and 2 for all three motors.

## Step 4
Fit each of the three motors onto the microscope body using two M4 screws.  It is possible that this step will be easier if you tap the holes in the microscope body first.  The screws should be done up tightly, otherwise the motor will wobble.

A motor screwed onto the microscope body

## Step 5
Fit the mini USB lead to the motor board, and fit the motor board into the case as shown.

The motor board, in its case

## Step 6
Connect the cables from the motors to the motor board as shown.

Motors connected to the motor board

## Step 7
Finally, sit the microscope on top of the motor board case, and tidy up the wiring using the cable ties.  You can more securely attach the motor board to the microscope using M3 screws at the corners, but you might want to wait until you have tested it in case you need to swap the wiring around.

The microscope complete with assembled motors

## Step 8
Congratulations, you have fitted the motors.  You will need to upload the motor controller firmware using the Arduino IDE.  Currently, the [firmware resides on github](https://github.com/rwb27/openflexure_nano_motor_controller).

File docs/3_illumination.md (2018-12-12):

# Assemble the illumination
The microscope usually works by looking at light that has passed through the sample - so we need to illuminate the sample from above.  This section takes you through the assembly of the illumination arm.

# Requirements
## Parts
*   1 [Illumination dovetail](./parts/illumination_dovetail)
*   1 [condenser arm](./parts/condenser)
*   1 [5mm LED](./parts/white_led) ideally wired up to a 2-way female header
*   2 [M3x8 cap head screws](./parts/m3x8mm_screws)
*   2 [M3 Washers](./parts/m3_washer)
*   1 [Condenser lens](./parts/condenser_lens) (optional)

## Tools
* 2.5mm hex key
* Condenser lens insertion tool (if using a condenser lens)

# Assembly Instructions
## Step 1
To build the condenser, you will need the two parts of the mounting arm, two M3 screws and washers, the LED & cable.  If you are using a condenser lens, you will also need the printed lens insertion tool to put the lens into the holder.

## Step 2
*This is an optional step.  If you are not using the condenser lens, skip to step 3*

Place the condenser lens on the insertion tool (flat side down), and push the condenser housing down onto it.  Take care to keep it vertical.  You may need to push fairly hard.  As with the tube lens in the optics module, check it's flat and push again if necessary.
The condenser module with the insertion tool



## Step 3
Insert the LED into the condenser housing.  It should push-fit and stay in place.  It can be glued or taped if it doesn't stay in.


## Step 4
Assemble the cable for the LED, if you don't have one soldered on already.  You just need to be able to light it up - we usually do this by soldering the LED to a resistor (about 80 ohms), then attaching about 20cm of cable with female crimps on the end.  This can easily be plugged onto the Raspberry Pi's 5v GPIO pin.

## Step 5
Place the illumination dovetail onto the platform on the microscope body, and secure in place with the two M3 screws.  Use a washer between the screw and the dovetail.  The holes on the microscope should be just the right size for the M3 screw, but you might need to use some force to get the screws in.  Be careful to stop turning the screws as soon as the dovetail is mounted tightly, though - otherwise you might damage the threads.

Mounting the illumination platform

## Step 6
Clip the horizontal part of the condenser onto the vertical dovetail.

Slide on the condenser

## Step 7
Neatly thread the cable for the LED through the gap between the condenser and the dovetail, and then down beside the optics module to the bottom of the microscope.  Don't pass it through the hole in the centre of the flat stage - pass it between the stage and the dovetail.

## Step 8
You have assembled the illumination - nearly there!

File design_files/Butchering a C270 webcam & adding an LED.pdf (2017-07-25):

1. Open the casing (there are two screws, accessible from the front I think)
2. Remove the PCB from the casing (it's held on by two screws) - retain the screws (as spares)
Snap the back of the case to remove it from the cable (the cable passes through a hole in the back of the case, so you have to snap the plastic with side cutters to remove it completely)

3.

De-solder the microphone from the circuit board (it's a cylindrical silver component with a black top, it's the biggest thing on the PCB).

4.

5. Unscrew the lens from the camera (retain the screws)
6. Using the screws from step 5, screw the PCB onto the bottom of the optics module
Unscrew the lens from its holder, and push-fit the lens, upside down (i.e. with the threaded part pointing upwards), onto the top of the optics module

7.

8. Solder one wire onto the ground pin of the PCB


Carefully scratch away the insulation on the red USB power wire using a scalpel or wire strippers. You're aiming to remove the insulation but NOT break the wire.
11. Solder another wire onto the exposed conductor on the USB power wire.
Gently pull the red USB power wire out of the connector. Slide on a small piece of heatshrink over the join and heat it up.

12.

13. Re-insert the USB power wire into the connector.
Use a blob of epoxy to attach the wires to the camera board; this is important to avoid the soldered connection snapping at an inconvenient moment.

14.

You may also want to epoxy the USB wires, as the power line will be weakened by your solder joint. I've not bothered so far…

15.

To use the C270 webcam with the OpenFlexure microscope:

The Logitech C270 is a handy, easy-to-get-hold-of webcam that I've often used in the OpenFlexure microscope. I have not properly documented how to dissassemble it, as it's fairly straightforward - but I thought it would be good to document how I tap into the power lines to power my LED (with series resistor). DO NOT TEST THIS ON YOUR COMPUTER!! If it is short-circuited, it will damage your motherboard. Use a Raspberry Pi or a hub first to check it lights up. I don't sell C270-based kits precisely because I am afraid of people wrecking their laptops…

DO THIS STRICTLY AT YOUR OWN RISK. I ACCEPT NO RESPONSIBILITY FOR FRIED USB PORTS!

# Butchering a C270 webcam & adding an LED

11 July 2017 14:43

July Page 1

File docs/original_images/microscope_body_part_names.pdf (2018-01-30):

### OpenFlexure Microscope: parts of the microscope body (LS65-M)


XY Table

Y actuator
housing

Z actuator
housing

X actuator
housing

legs

motor lugs (x6)

nut trap (x3)

motor lugs (x6)

XY Table

flexures (thin parts) mounting lugs (x2)

illumination dovetail | actuators (x3)

objective
z axis struts (x2) | clip

Richard Bowman, Jan 2018

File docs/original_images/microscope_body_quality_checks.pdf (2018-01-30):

# OpenFlexure Microscope: quality checks

## Richard Bowman, Jan 2018


1. Check the XY table printed OK. Some loops of plastic
underneath are ok, but the top must be flat.
2. Check the X and Y
actuators move when
pushed with a finger, and
that the XY table moves
with the actuator.


push | push

this part moves


push

3. Check the Z actuator moves
when pushed with a finger, and that the objective clip moves with the actuator. If it doesn't, it may be that the printer overextruded, so the gaps
between the Z struts and the body are not present. This can often be fixed with a craft knife.
4. Check the objective clip is vertical and that the front of the clip is straight. There is often a kink at the very top if it has wobbled during printing.


6. Check that the hooks at the top of the actuator columns have printed correctly (this is most easily checked by inserting the band, as shown in instructions).
6. Check that the nut traps are large enough to insert an M3 nut. You should be able to push it in using the nut insertion tool, as shown in the instructions. The hole in the nut should line up with the hole in the actuator column.
7. Check that the flexures at the tops of the leg printed correctly. There should be 4 thin sections without a strut either above or below them (red arrows). These are important for the XY table to be able to move. The small strut at


the top should be in the middle of the two legs, and its outer edge should line up with the legs (blue rectangles).

6. Check that the optics module fits into the objective clip. It should take some force to insert the module, but not so much that it breaks the plastic - see the instructions for details. You may snap the thin flat part at the bottom to make this easier.

insert
optics
module

snap

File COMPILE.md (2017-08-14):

# OpenFlexure Microscope: Compiling from source

The microscope is modelled using OpenSCAD.  This means there's a collection of scripts that, when run, generate STL files that you can then print.  The best way to get hold of the latest STL files is to generate them yourself.  To do this, you will need [OpenSCAD](http://www.openscad.org/) (available for Windows, Mac and Linux).  The simplest way to build all the necessary STL files is to use GNU Make.  If you use Linux you will almost certainly have this, Mac OS should either have it or be able to get it from homebrew etc., and Windows you can get it through Cygwin or MinGW.

To build all the STL files (NB you don't need to print all of these, there are some alternatives), simply change directory to the root folder of this repository and run ``make all``.  This will compile the files and put them in the ``builds/`` directory.

## Make on Windows
I was happy to find out that [you can use make in MSYS](https://gist.github.com/evanwill/0207876c3243bbb6863e65ec5dc3f058), which comes bundled with Git for Windows. If you install Git for Windows, you can then download a copy of the executable file for make and put it in the bin directory.  For me, this was ``C:\Users\me\AppData\Local\Programs\Git\mingw64\bin`` though your installation may be different.  NB to start MSYS on Windows, look for "Git Bash" in your Start menu.

## OpenSCAD command line
You'll need to make sure OpenSCAD is in your executable path so the build script can [run it from the command line](https://en.wikibooks.org/wiki/OpenSCAD_User_Manual/Using_OpenSCAD_in_a_command_line_environment).  This is probably the case on Linux, but on Windows I just ran ``PATH="$PATH:/c/Program Files/OpenSCAD/"`` before running make.  A more permanent solution is to put that command line into a text file ``.bash_profile`` in your home directory (i.e. ``C:\Users\me\.bash_profile``).  If it doesn't exist, just create a new text file with that as the only line.  Once you've done this, OpenSCAD will automatically be added to your path every time you start MSYS (aka Git Bash).  NB the filename does not have a ``.txt`` extension, and it won't work if you leave one there.  Symlinking the OpenSCAD binary into your mingw64 binaries folder seems to break things like the OpenSCAD includes directory, so use the method above in preference if you can.

On mac, you may need to add a symlink as well, probably from ``/usr/local/bin/openscad`` -> ``/Applications/OpenSCAD.app/Contents/MacOS/OpenSCAD`` (I've not checked these paths but they should be approximately right).

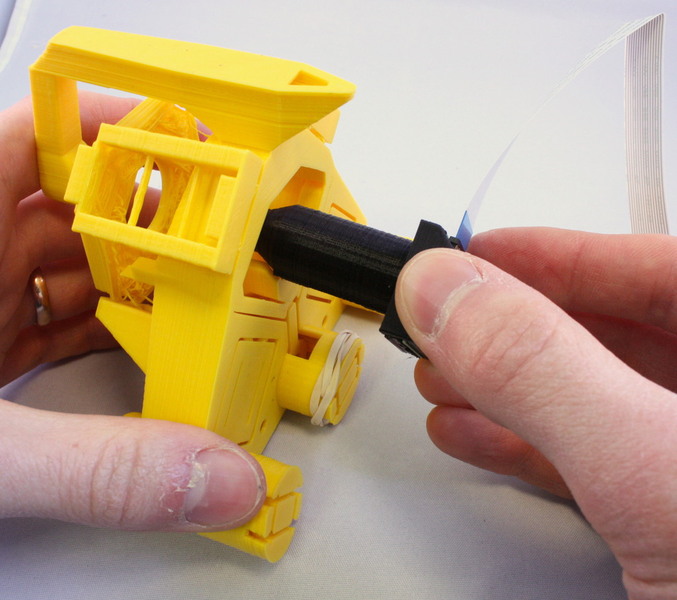
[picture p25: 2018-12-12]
docs/images/optics_insertion_1.jpg

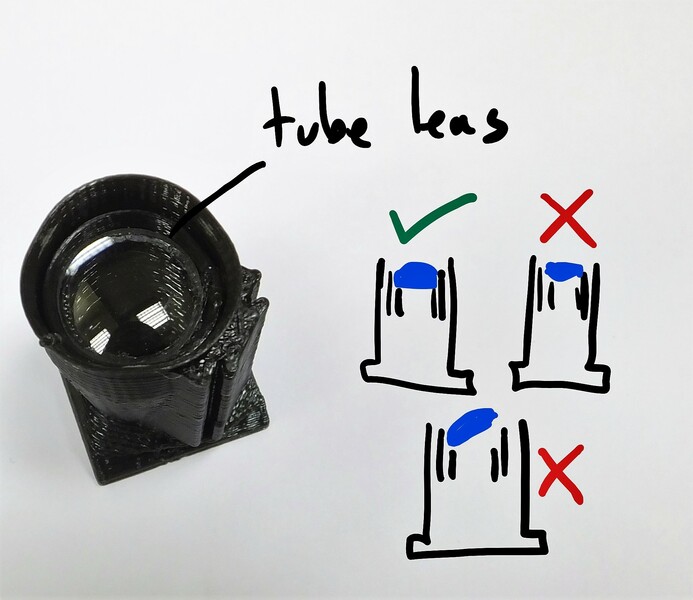
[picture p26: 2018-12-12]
docs/images/hires_optics_tubelens_2.jpg

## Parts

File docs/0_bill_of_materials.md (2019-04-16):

# Obtaining the non-printed parts
Make sure you have all the necessary parts and tools before you start.  The parts should all be listed in the bill of materials below, which is currently a work in progress (eventually it will be produced automatically, which should help it to stay accurate).  We recommend reading through all the instructions and checking that the quantities shown here add up correctly, until auto-generation is working.  Printed parts are described in the [next section](./0_printing.md).

## Fixing hardware:
*   3x [M3x25mm hexagon head screws](./parts/fixings/m3x25mm_hexagonhead_screw.md), stainless steel
*   3x [M3 brass nut](./parts/fixings/m3_brass_nut.md)
*   1x [M3 steel nut](./parts/fixings/m3_steel_nut.md) (using brass is also fine)
*   8x [M3 stainless steel washer](./parts/fixings/m3_washer.md)
*   3-14x [M3x8mm cap head screw](./parts/fixings/m3x8mm_caphead_screw.md) (some ar optional, for sample clips and sample riser, but you will need at least three)
*   2-4x [M2x6mm cap head screws](./parts/fixings/m2x6mm_caphead_screw.md) 
*   6x [M4x6mm button head screws](./parts/fixings/m4x6mm_buttonhead_screw.md) (optional, for motors)
*   3x [Viton O-ring, 30x2mm](./parts/fixings/viton_o_ring_30mm_inner_diameter_2mm_cross_section.md) (NB: get some spares!)

## Electronic parts:
*   [5mm White LED](./parts/electronics/white_led.md)
*   [60 Ohm resistor](./parts/electronics/60_ohm_resistor.md)
*   [Stranded wire](./parts/electronics/stranded_wire.md)
*   [2-way JST header connector](./parts/electronics/2_way_jst_header.md) (so long as you have some way of lighting up the LED, it doesn't much matter)
*   [Raspbery Pi camera module](./parts/electronics/raspberry_pi_camera.md) (v2, though v1 works too)
*   [Raspberry Pi](./parts/electronics/raspberry_pi.md) (with associated power supply, keyboard, monitor, etc.)
*   3x [28BYJ-48 micro stepper motors](./parts/electronics/micro_geared_stepper.md) (optional)
*   [Motor driver board](./parts/electronics/sangaboard.md) for the above (optional)

## Optical parts:
*   [13mm diameter, 5mm focal length plastic condenser lens](./parts/optics/condenser_lens.md) (optional, strongly recommended for high resolution optics)
*   [12.7mm diameter, 50mm focal length achromatic lens](./parts/optics/tube_lens.md) (for high resolution optics only)
*   [RMS threaded, finite-conjugates microscope objective](./parts/optics/microscope_objective.md) (for high resolution optics only)

## Tools:
*   2.5mm hex key
*   1.5mm hex key (to secure the camera using M2 screws)
*   tape (electrical tape or PTFE plumbers tape work nicely, though regular sticky tape is also fine)
*   sharp craft knife (for trimming tape and cleaning up the print)
*   3mm drill bit in hand chuck (if you printed the parts yourself and need to open out the holes)
*   needle nose pliers (optional, but useful - particularly good for cleaning up prints)

Don't forget the raspberry pi, camera module, and associated screen, power supply, SD card, keyboard, mouse, etc. (I have not listed these explicitly, but they're needed to run the Pi). Also, if you use the high resolution optics module or want to add motors, you will need additional parts.

While you're waiting for any parts you have ordered to arrive, why not try the next section on [printing the plastic parts](./0_printing.md).

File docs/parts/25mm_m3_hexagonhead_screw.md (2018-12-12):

# 25mm M3 Hexagon-head screw
25mm M3 Hexagon-head screw

## Details
*   **Supplier:** Anglian Fasteners Limited
*   **Supplier's part number:** 6663
*   **URL:** http://www.anglianfasteners.co.uk/
*   **Material units:** NONE

# Manufacturing Instructions
## Step

These screws are used as the lead screws for the stage; stainless steel is probably best.  The hexagon head fits into a socket on the plastic gears, which is important as the gear needs to rotate the screw.

If hexagon-head screws are not available, a good substitute is to screw a nut tightly against the head of a screw (with whatever head type you can get hold of).  The nut will then take the place of the hexagon head and the screw can still be turned by the thumbwheel or gear.  It's best to use a 30mm screw for the central actuator, and a 25mm screw for each of the two outer actuators if you're going to make that substitution.

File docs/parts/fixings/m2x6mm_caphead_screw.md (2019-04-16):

# M2x6mm screws

## Details
*   **Supplier:** Anglian Fasteners Limited
*   **Supplier's part number:** 
*   **URL:** http://www.anglianfasteners.co.uk/
*   **Material units:** NONE

These screws attach the Raspberry Pi camera board to the optics module.  Two are required, using four is optional but slightly more robust.

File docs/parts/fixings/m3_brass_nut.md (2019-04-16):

# M3 Brass Nut
M3 Brass Nut

## Details
*   **Supplier:** Anglian Fasteners Limited
*   **Supplier's part number:** 11355
*   **URL:** http://www.anglianfasteners.co.uk/
*   **Material units:** NONE

# Manufacturing Instructions
## Step
These nuts form part of the actuator.  Brass ones will have less friction and result in smoother motion.  Steel nuts are used elsewhere for fastening, but can be easily substituted with a brass nut.

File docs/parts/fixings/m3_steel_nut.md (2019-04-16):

# M3 Steel Nut
M3 Steel Nut

## Details
*   **Supplier:** Anglian Fasteners Limited
*   **Supplier's part number:** 
*   **URL:** http://www.anglianfasteners.co.uk/
*   **Material units:** NONE

Steel nuts are used as fasteners in various parts of the microscope.  There is no need to use brass for these, and brass is more expensive.  However, if you only want to buy one box of nuts, it's fine to buy only brass ones.

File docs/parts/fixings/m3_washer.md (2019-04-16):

# M3 Washer
M3 Washer

## Details
*   **Supplier:** Anglian Fasteners Limited
*   **Supplier's part number:** 7118
*   **URL:** http://www.anglianfasteners.co.uk/
*   **Material units:** NONE

The washers fit between the gears and the microscope to provide a metal bearing surface.  It's important to use two washers under each gear, so that the friction occurs between two metal surfaces rather than between plastic and metal surfaces.  Additional washers are used as fasteners, e.g. for the adjustable illumination arm.  We recommend steel washers.

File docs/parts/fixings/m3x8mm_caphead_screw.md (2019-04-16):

# M3x8mm screws

## Details
*   **Supplier:** Anglian Fasteners Limited
*   **Supplier's part number:** 14315
*   **URL:** http://www.anglianfasteners.co.uk/
*   **Material units:** NONE

These screws attach the sample clips, optics module, illumination, and various other parts.  Exactly how many you need will depend on microscope options - it's safest to make sure you have a handful.  These don't need to be particularly fine quality, but cap head (i.e. driven with a hex key) will make some steps easier, particularly inserting the optics module.

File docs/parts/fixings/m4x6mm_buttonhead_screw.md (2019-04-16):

# M4x6mm screws

## Details
*   **Supplier:** Anglian Fasteners Limited
*   **Supplier's part number:** 
*   **URL:** http://www.anglianfasteners.co.uk/
*   **Material units:** NONE

These screws attach the motors in the motorised version of the microscope.  We have suggested button-head screws because they look neat and mean you can use the same 2.5mm hex driver that fixes nearly everything else on the microscope.  However, any M4 screw will do, provided it's not longer than about 8mm.

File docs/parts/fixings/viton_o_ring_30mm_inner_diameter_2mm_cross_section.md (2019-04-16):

# Viton O ring, 30mm inner diameter, 2mm cross section

## Details
*   **Material:** Viton or Nitrile
*   **Inner diameter:** 30mm
*   **Cross-section:** 2mm
*   **Outer diameter:** 34mm
*   **Supplier website:** [http://www.simplybearings.co.uk/]

The O-rings function as springs, to provide a return force on the nut that is pulled upwards by the screw.  I use Viton O-rings, 30mm ID, as they provide about the right force.  You can substitute for rubber bands, but it's difficult to specify the size directly, and they tend to perish and snap in a few weeks.  Viton O rings are well worth the effort and price!

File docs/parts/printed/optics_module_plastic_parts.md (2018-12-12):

# Optics module plastic parts
Optics module plastic parts

## Details
*   **Material used:** 0.01
*   **Material units:** KG

## Media
*   
*   
*   
*   
*   
*   
*   

# Manufacturing Instructions
## Step
There are several versions of the optics module, depending on your camera (Raspberry Pi Camera v2, Logitech C270, or WaterScope USB camera) and on whether you will use the lens from the camera (pilens, M12, ownlens) or an RMS objective and 40mm tube lens.  Make sure you pick the right STL file for your camera module!  There is a cover that fits over the Raspberry Pi camera module, and holds it firmly onto the optics module.

## Step
The optics module needs to print with some fine detail, so the dovetail meshes nicely with the stage.  A good way to ensure this is to print it at the same time as other parts - either print more than one optics module at a time, or print it at the same time as the microscope body.  This slows down the time for each layer, and means the plastic can cool more completely before the layer on top is deposited, resulting in a higher-quality part.  The optics module is best printed in black to cut down on stray light inside the tube - though it will still work in other colours.

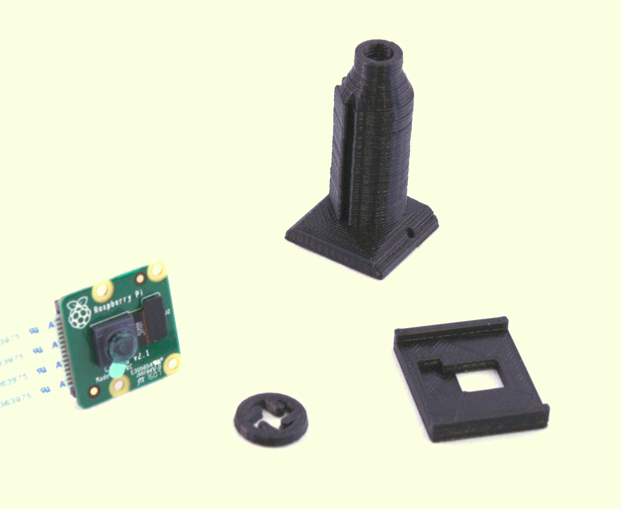
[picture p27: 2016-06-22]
docs/original_images/optics_module_parts.jpg

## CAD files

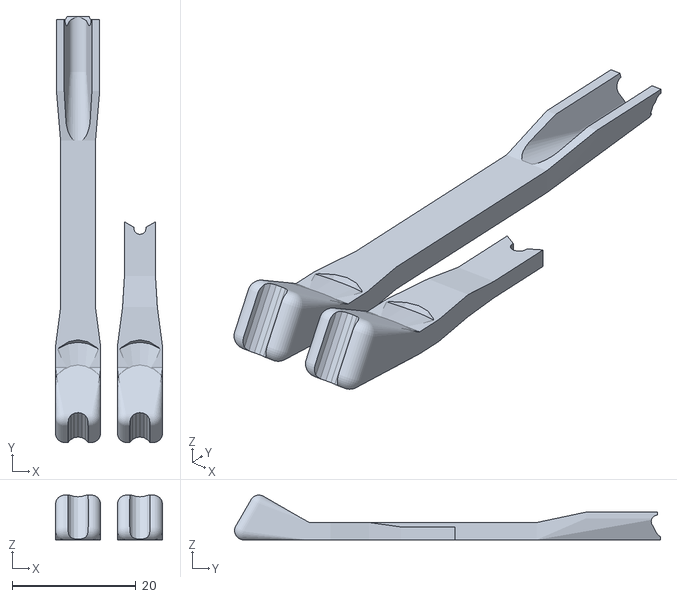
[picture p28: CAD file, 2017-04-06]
stl/actuator_assembly_tools_notched.stl
17.3 x 68.8 x 7.24

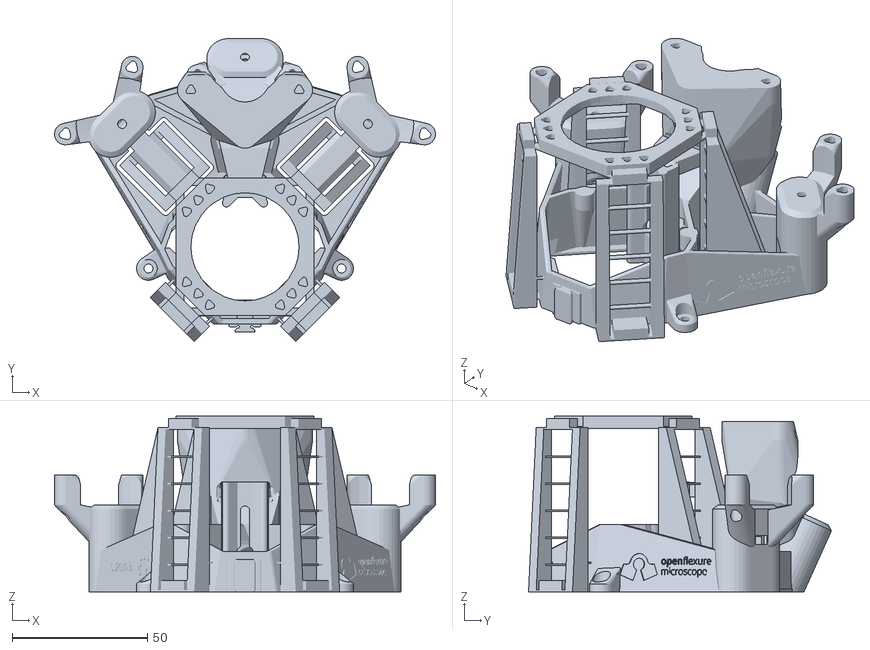
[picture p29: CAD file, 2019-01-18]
builds/main_body_LS65-M_fixed.obj
140.9 x 112.1 x 65.0

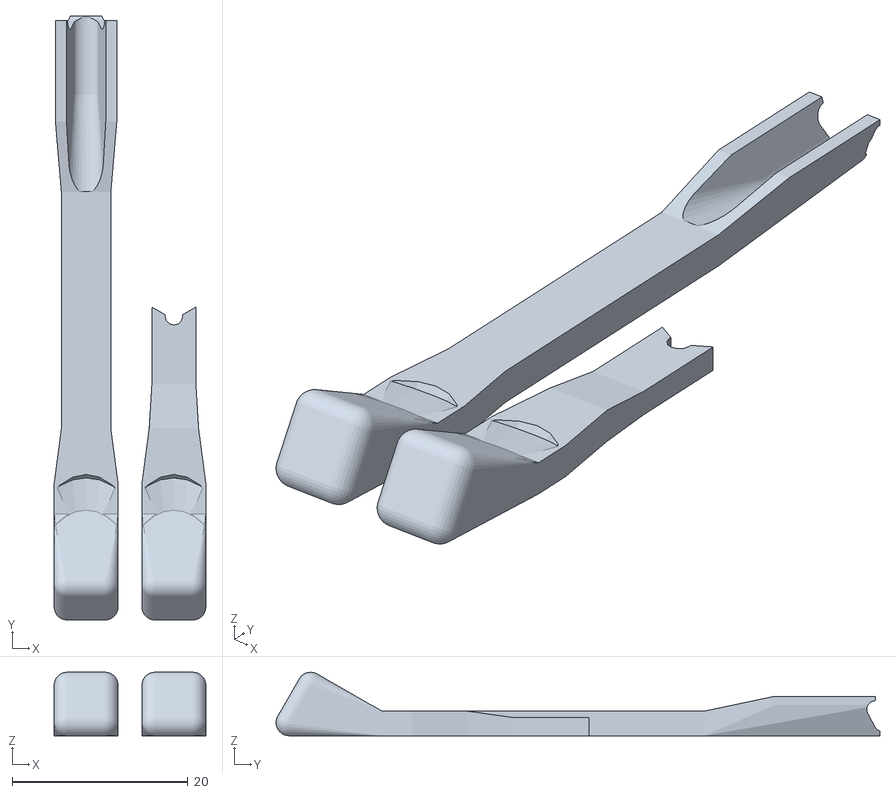
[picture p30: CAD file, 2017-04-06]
stl/actuator_assembly_tools.stl
17.3 x 68.8 x 7.24

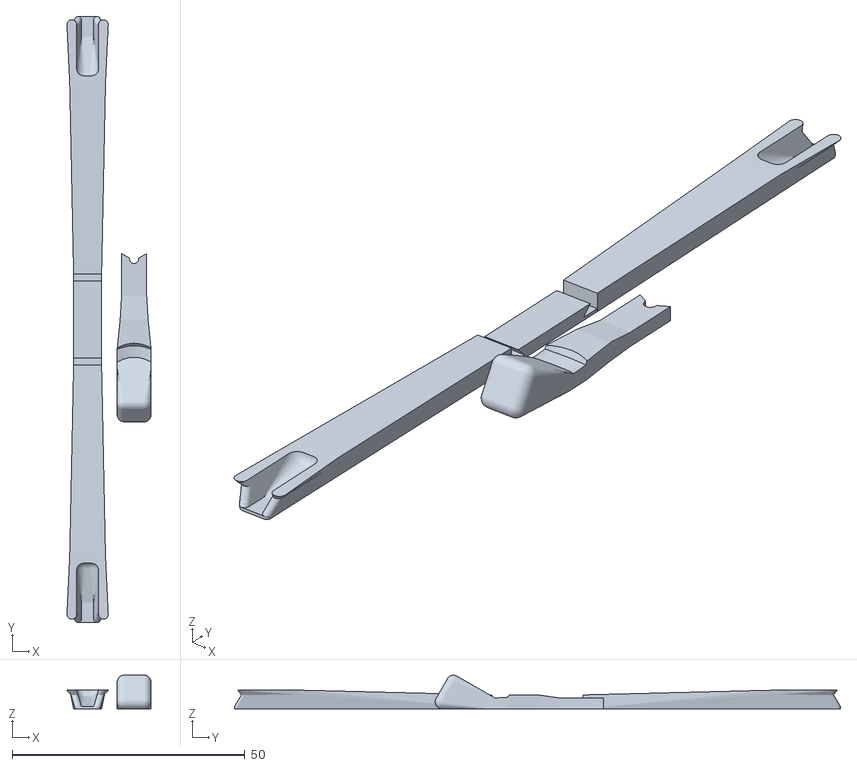
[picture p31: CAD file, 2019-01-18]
builds/actuator_assembly_tools.stl
18.1 x 130.2 x 7.24

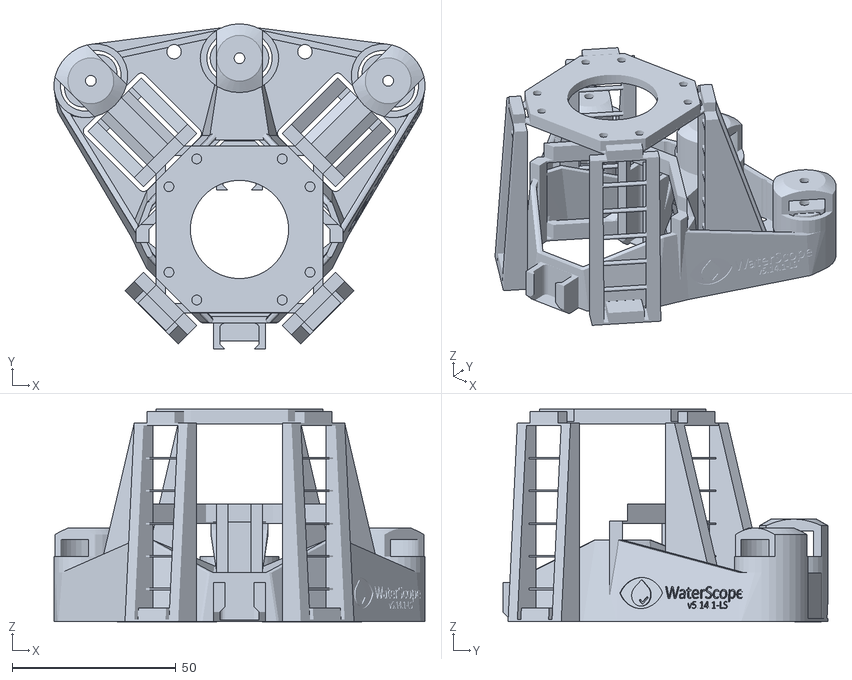
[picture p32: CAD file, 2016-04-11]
stl/main_body_LS65.stl
113.4 x 99.4 x 65.0

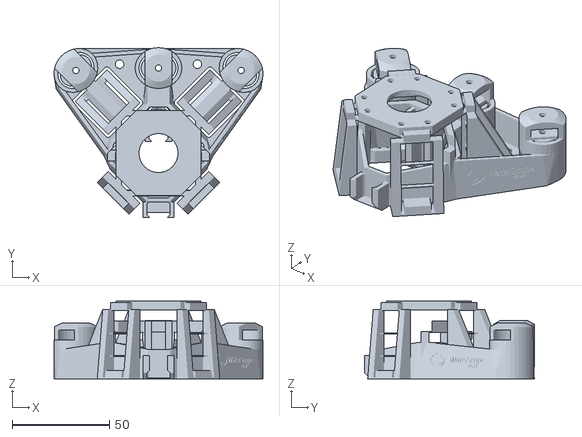
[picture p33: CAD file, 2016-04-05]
stl/main_body_vanilla.stl
107.4 x 87.2 x 40.0

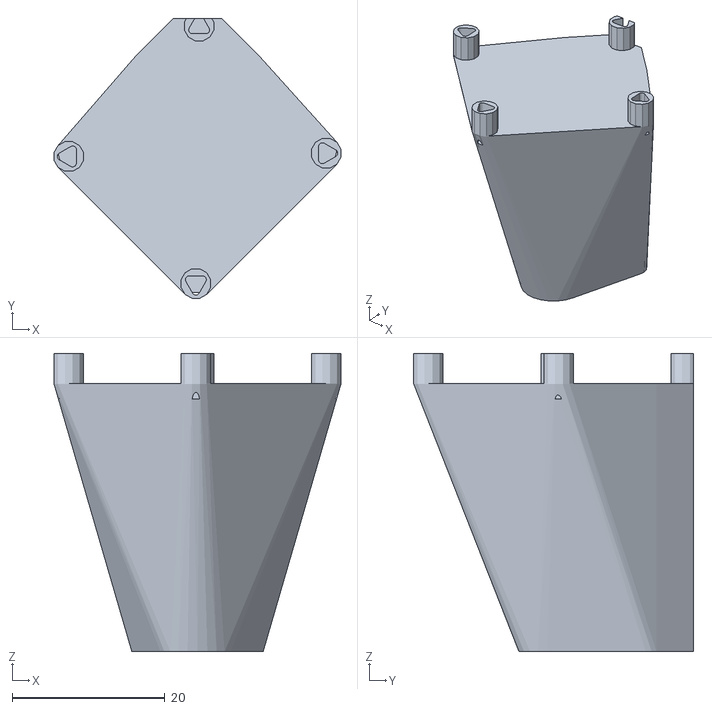
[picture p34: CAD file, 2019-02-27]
builds/camera_platform_6led_LS65.stl
37.5 x 36.6 x 39.0

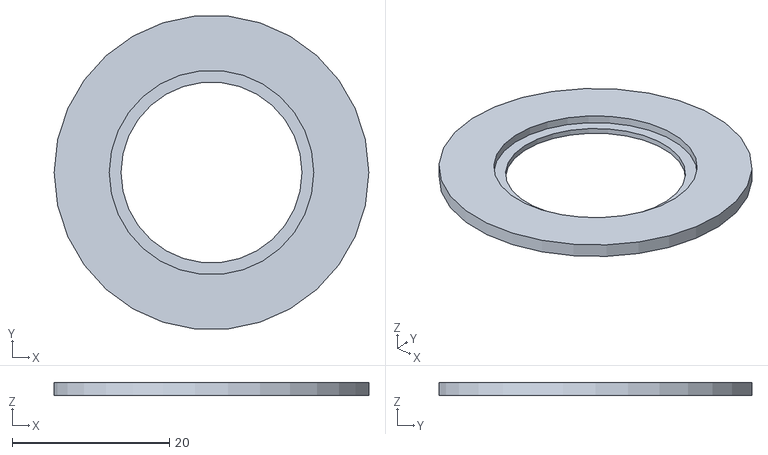
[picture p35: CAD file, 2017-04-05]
openscad/adapters/1_inch_disc_holder.stl
40.0 x 39.8 x 1.70

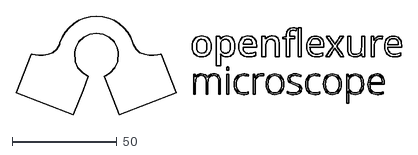
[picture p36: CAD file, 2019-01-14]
openscad/openflexure_logo.dxf
184.0 x 47.3

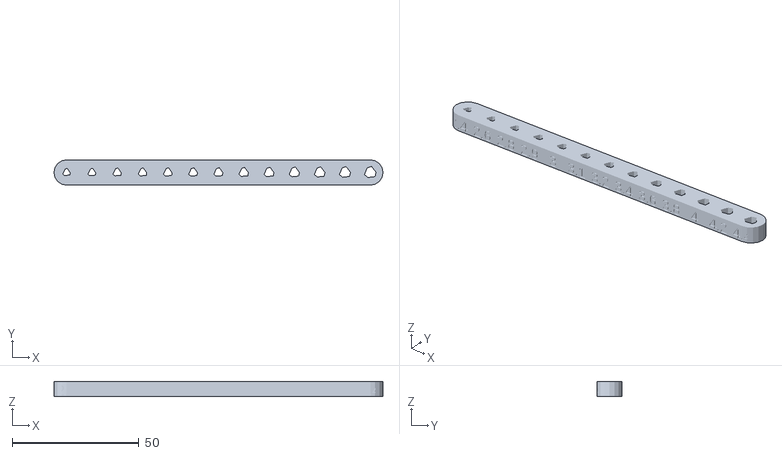
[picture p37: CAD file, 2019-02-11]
stl/trylinder_selftap_holes_test.stl
130.0 x 10.0 x 6.00

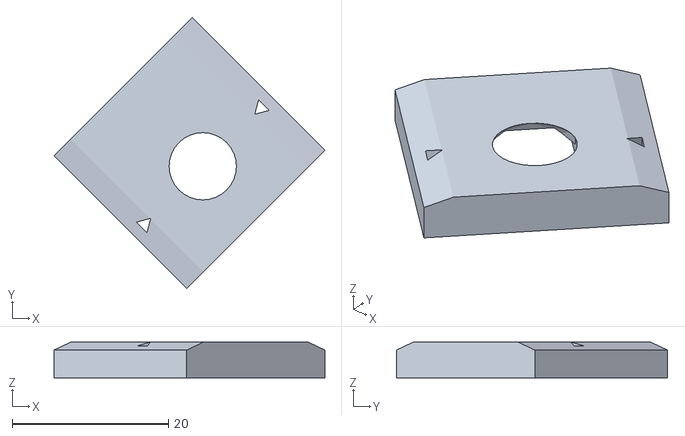
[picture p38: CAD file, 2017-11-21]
test.stl
34.6 x 34.6 x 4.55

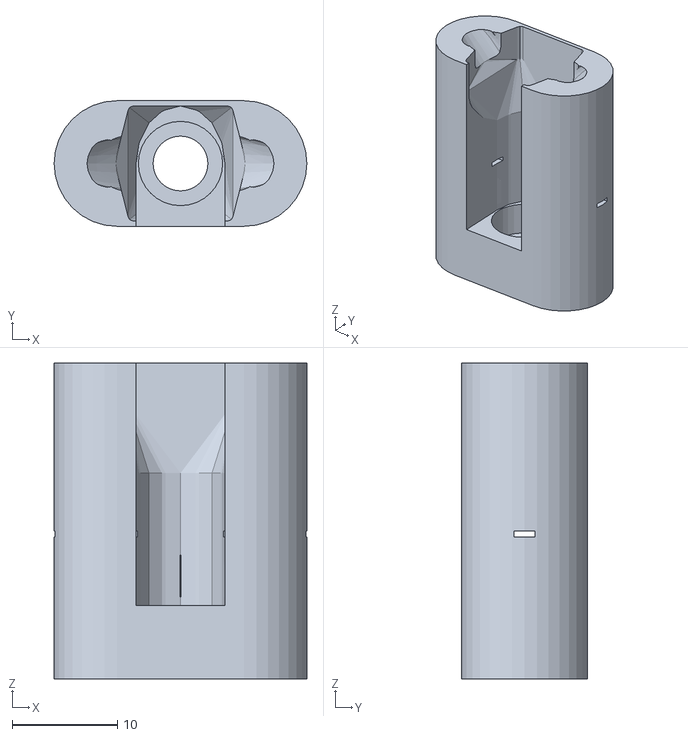
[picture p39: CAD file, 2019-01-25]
builds/actuator_drilling_jig.stl
24.0 x 11.9 x 30.0

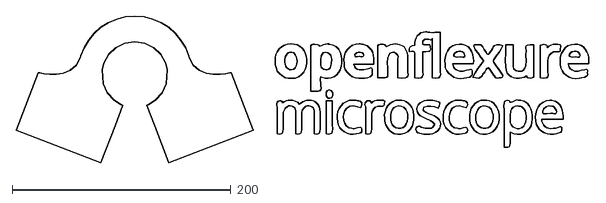
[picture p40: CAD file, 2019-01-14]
openscad/openflexure_logo_outset.dxf
524.2 x 134.0

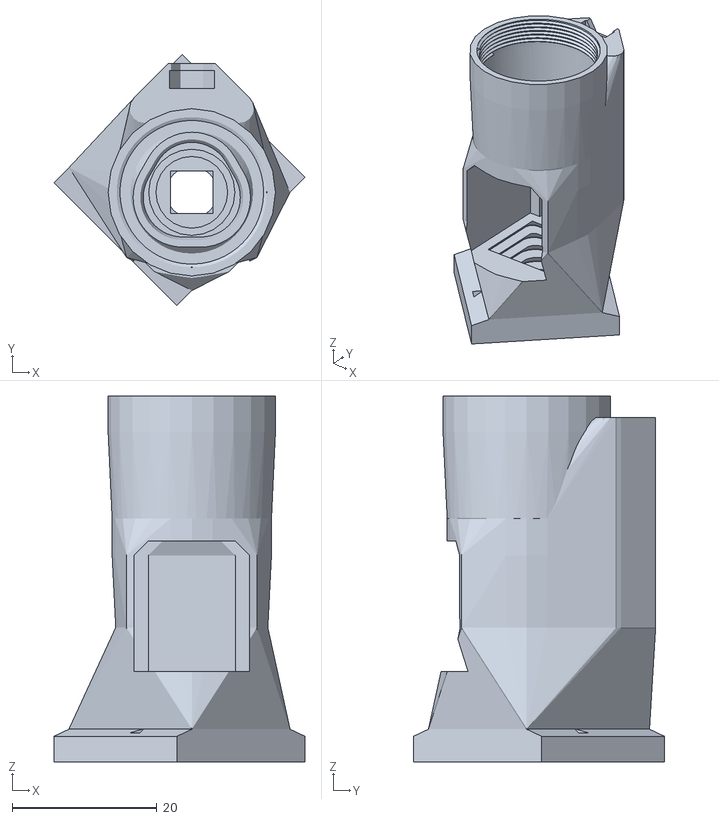
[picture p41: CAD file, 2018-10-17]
stl/optics_picamera_rms_f50d13_fl.stl
34.6 x 34.6 x 50.5

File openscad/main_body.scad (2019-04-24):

/******************************************************************
*                                                                 *
* OpenFlexure Microscope: Microscope body                         *
*                                                                 *
* This is the chassis of the OpenFlexure microscope, an open      *
* microscope and 3-axis translation stage.  It gets really good   *
* precision over a ~10mm range, by using plastic flexure          *
* mechanisms.                                                     *
*                                                                 *
* (c) Richard Bowman, January 2016                                *
* Released under the CERN Open Hardware License                   *
*                                                                 *
******************************************************************/

use <./utilities.scad>;
use <./compact_nut_seat.scad>;
use <./logo.scad>;
use <./dovetail.scad>;
use <./z_axis.scad>;
use <./gears.scad>;
use <./wall.scad>;
use <./main_body_transforms.scad>;
include <./microscope_parameters.scad>; //All the geometric variables are now in here.


module leg(brace=stage_flex_w){
    // The legs support the stage - this is either used directly
    // or via "actuator" to make the legs with levers
    fw=stage_flex_w;
	union(){
       	//leg
		reflect([1,0,0]){
			//vertical legs
			translate([leg_middle_w/2+zflex_l,0,0]) hull(){
				cube(leg);
				cube([leg[0],fw+brace,d]); //extend it to be a triangle
			}

            //flexure bridges between the legs
            zs = [flex_z1, flex_z2]; //heights of bridges between legs
            bs = [brace, 0]; //"brace positions" - a nonzero value here
                             //widens the leg, and adds another flexure
                             //at the new position.  bs[i]=fw will double
                             //the width of the flexure, while a larger 
                             //value produces two distinct flexures.
			for(i=[0,1]) translate([0,0,zs[i]]){
				translate([-d,0,0]) hull() repeat([0,bs[i],0],2) //solid part
                        cube([leg_middle_w/2+d,leg[1],stage_t-0.2*leg[1]]);
				translate([-d,0,0]) repeat([0,bs[i],0],2) //flexures
                        cube([leg_middle_w/2+zflex_l+leg[0],leg[1],zflex_t]);
			}
		}
        
		//thin links between legs
		if(flex_z2-flex_z1 > 2*bridge_dz){
			n=floor((flex_z2-flex_z1)/bridge_dz);
			dz=(flex_z2-flex_z1)/n;
			translate([0,leg[1]/2,flex_z1+dz]) repeat([0,0,dz],n-1) cube([leg_outer_w,2,0.5],center=true);
		}
	}
}
module actuator(){
    // A leg that supports the stage, plus a lever to tilt it.
    // No longer includes the flexible nut seat actuating column.
    // TODO: find the code that unifies this with leg()
	brace=20;
    fw=stage_flex_w;
    w = actuator[0];
    union(){
        leg(brace=brace);

		//arm (horizontal bit)
		difference(){
            sequential_hull(){
                translate([-leg_middle_w/2,0,0]) cube([leg_middle_w,brace+fw,4]);
                translate([-w/2,0,0]) cube([w,brace+fw+0,actuator[2]]);
                translate([-w/2,0,0]) cube(actuator);
            }
            //don't foul the actuator column
            translate([0,actuating_nut_r,0]) actuator_end_cutout(); 
        }

	}
}
module actuator_silhouette(h=999){
    // This defines the cut-out from the base structure for the XY
    // actuators.
    linear_extrude(2*h,center=true) minkowski(){
        circle(r=zflex_l,$fn=12);
        projection() actuator();
    }
}

module back_foot_mounting_screw(d=3*0.95, h=16, center=true){
    translate([0,illumination_clip_y+3,0]) cylinder(d=d, h=h,center=center);
}

module mounting_hole_lugs(){
    // lugs either side of the XY table to bolt the microscope down
    //these are to mount onto the baseplate 
    for(p=base_mounting_holes) {
        if(p[1]<0 && p[0]>0) reflect([1,0,0]) hull(){
            translate([z_flexure_x,0,0]) rotate(-120) cube([10,d,10]);
            translate(p) cylinder(r=4*1.1,h=3);
        }
    }
}

module xy_limit_switch_mount(d=3.3*2, h=6){
    // A mount for the XY limit switch (M3)
    leg_frame(45) translate([-9, -zflex_l-zawall_h*sin(6)-3.3+1, zawall_h-6]) cylinder(d=d,h=h);
}


// The "wall" that forms most of the microscope's structure
module wall_inside_xy_stage(){
    // First, go around the inside of the legs, under the stage.
    // This starts at the Z nut seat.  I've split it into two
    // blocks, because the shape is not convex so the base
    // would be bigger than the walls otherwise.
    reflect([1,0,0]) sequential_hull(){
        //inner_wall_vertex(-45, -leg_outer_w/2-wall_t/2, zbwall_h);
        mirror([1,0,0]) z_bridge_wall_vertex();
        z_bridge_wall_vertex();
        inner_wall_vertex(45, -leg_outer_w/2, zawall_h);
        z_anchor_wall_vertex();
        inner_wall_vertex(135, leg_outer_w/2, zawall_h);
        inner_wall_vertex(135, -leg_outer_w/2, wall_h);
        inner_wall_vertex(-135, leg_outer_w/2, wall_h);
    }
}

module wall_outside_xy_actuators(){
    // Add the wall from the XY actuator column to the middle
    sequential_hull(){
        z_anchor_wall_vertex(); // join at the Z anchor 
        // [nb this is no longer actually the z anchor since the new z axis]
        // anchor at the same angle on the actuator
        // NB the base of the wall is outside the
        // base of the screw seat
        leg_frame(45) translate([-ss_outer()[0]/2+wall_t/2,actuating_nut_r,0]){
            rotate(-45) wall_vertex(y_tilt=atan(wall_t/zawall_h));
        }
    }
}

module wall_inside_xy_actuators(){
    // Connect the Z anchor to the XY actuators
    hull(){
        translate([-(z_anchor_w/2+wall_t/2+1), z_anchor_y + 1, 0]) 
                     wall_vertex();
        y_actuator_wall_vertex();
    }
}

module wall_between_actuators(){
    // link the actuators together
    hull(){
        y_actuator_wall_vertex();
        translate([0,z_nut_y+ss_outer()[1]/2-wall_t/2,0]) wall_vertex();
    }
}

///////////////////// MAIN STRUCTURE STARTS HERE ///////////////
exterior_brim(r=2);
difference(){
union(){

	//legs (incl. actuators)
	reflect([1,0,0]) leg_frame(135) leg();
	each_actuator(){
        actuator();
		translate([0,actuating_nut_r,0]) actuator_column(h=actuator_h, join_to_casing=true);
    }
	//flexures connecting bottoms of legs to centre
	each_leg() reflect([1,0,0]) translate([0,0,flex_z1]){
        w=stage_flex_w;
        translate([leg_middle_w/2-w,0,0.5]) hull()
			repeat([1,-1,0]*(zflex_l+wall_t/2),2) cube([w,d,zflex_t]);
    }
    //tie the legs to the wall (built later) during printing
    reflect([1,0,0]) leg_frame(135) reflect([1,0,0]) {
        translate([leg_middle_w/2+zflex[1]+zflex[0]/2, -wall_h*0.7*tan(6)-1-zflex[1], wall_h*0.7]) cube([1, wall_h*0.7*tan(6)+2+zflex[1], 0.5]);
    }

	// flexures between legs and stage
    // NB these connect the legs together, and pass all the way under the stage.  This
    // is important, if they get cut then the bridges will fail!
	difference(){
		hull() each_leg() translate([0,0,flex_z2+zflex_t/2+0.5]) cube([leg_middle_w,d,zflex_t],center=true);
		hull() each_leg() cube([leg_middle_w-2*stage_flex_w,d,999],center=true);
	}

	//stage
   // this must get built up carefully: we start with the bridges round the edge, then work inwards.
	difference(){
		hull() each_leg() translate([0,-zflex_l-d,flex_z2+1+(stage_t-1)/2]) cube([leg_middle_w+2*zflex_l,2*d,stage_t-1],center=true); //hole in the stage
        intersection(){
            // This cuts out the hole in the stage, starting from a square.
            // The intersection restricts it to the space between the bridges, to avoid any
            // holes in the sides of the stage.
            translate([0,0,flex_z2+0.5+0.5]) rotate(45) hole_from_bottom(hole_r,h=999);
            hull() each_leg() cube([leg_middle_w-2*stage_flex_w,d,999],center=true);
        }
		each_leg() translate([0,-zflex_l-4,flex_z2+1.5]) repeat([leg_middle_w/2,0,0],3,center=true) trylinder_selftap(3,h=999); //mounting holes
	}
	
	//z axis
    z_axis_flexures();
    z_axis_struts();
    objective_mount();
    z_actuator_column();
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

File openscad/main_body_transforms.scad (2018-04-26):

/******************************************************************
*                                                                 *
* OpenFlexure Microscope: Microscope body transforms              *
*                                                                 *
* Various transforms used in the microscope.                      *
*                                                                 *
* (c) Richard Bowman, January 2016                                *
* Released under the CERN Open Hardware License                   *
*                                                                 *
******************************************************************/

use <./utilities.scad>;
use <./compact_nut_seat.scad>;
include <./microscope_parameters.scad>;

module shear_x(amount=1){
    // Shear transformation: tilt the Y axis towards the X axis
    // e.g. if amount=1, then a straight line in Y will be
    // tilted to 45 degrees between X and Y, while X lines are
    // unchanged.  This is used in the Z axis.
	multmatrix([[1,amount,0,0],
					 [0,1,0,0],
					 [0,0,1,0],
					 [0,0,0,1]]) children();
}


module leg_frame(angle){
    // Transform into the frame of one of the legs of the stage
	rotate(angle) translate([0,leg_r,]) children();
}
module each_leg(){
    // Repeat for each of the legs of the stage
	for(angle=[45,135,-135,-45]) leg_frame(angle) children();
}
module each_actuator(){
    // Repeat this for both of the actuated legs (the ones with levers)
	reflect([1,0,0]) leg_frame(45) children();
}

module place_on_wall(){
    //this is a complicated transformation!  The wall runs from
    wall_start = [z_flexure_x+wall_t/2,-wall_t/2,0]; // to
    wall_end = ([1,1,0]*(leg_r+actuating_nut_r)
                 +[1,-1,0]*(ss_outer()[0]/2-wall_t/2))/sqrt(2);
    wall_disp = wall_end - wall_start; // vector along the wall base
    // pivot about the starting corner of the wall so X is along it
    translate(wall_start) rotate(atan(wall_disp[1]/wall_disp[0]))
    // move out to the surface (the above are centres of cylinders)
    // and then align y with the vertical axis of the wall
    translate([0,-wall_t/2,0]) rotate([90-atan(wall_t/zawall_h/sqrt(2)),0,0])
    // now X and Y are in the plane of the wall, and z=0 is its surface.
    children();
}

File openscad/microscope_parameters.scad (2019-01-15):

/******************************************************************
*                                                                 *
* OpenFlexure Microscope: Microscope Parameters                   *
*                                                                 *
* This is the top-level configuration file for the OpenFlexure    *
* microscope, an open microscope and 3-axis translation stage.    *
* It gets really good precision over a ~10mm range, by using      *
* plastic flexure mechanisms.                                     *
*                                                                 *
* Generally I've tried to put parts (or collections of closely    *
* related parts) in their own files.  However, all the parts      *
* depend on the geometry of the microscope - so these parameters  *
* are gathered together here.  In general, the ones you might     *
* to change are towards the top!  Lower-down ones are defined in  *
* terms of higher-up ones - confusion might arise if you redefine *
* these later...                                                  *
*                                                                 *
* (c) Richard Bowman, January 2016                                *
* Released under the CERN Open Hardware License                   *
*                                                                 *
* http://www.github.com/rwb27/openflexure_microscope              *
* http://www.docubricks.com/projects/openflexure-microscope       *
* http://www.waterscope.org                                       *
*                                                                 *
******************************************************************/

d = 0.05;
$fn=32;

// These are the most useful parameters to change!
big_stage = true; //this option is obsolete and must now always be true...
motor_lugs = true;
endstops = false; //motor_lugs;
version_numstring = "5.20.0-b";
camera = "picamera_2"; //see cameras/camera.scad for valid values
optics = "pilens"; //see optics.scad for valid values
led_r = 5/2; //size of the LED used for illumination
feet_endstops = true;
beamsplitter = false; //enables a cut-out in some optics modules for a beamsplitter


// This sets the basic geometry of the microscope
sample_z = big_stage?65:40; // height of the top of the stage
leg_r = big_stage?30:25; // radius of innermost part of legs (stage size)
hole_r = big_stage?20:10; // size of hole in the stage
xy_lever_ratio = big_stage?4.0/7.0:1.0; // mechanical advantage of actuator over stage - can be used to trade speed and precision
z_lever_ratio = 1.0; // as above, for Z axis (must be >1)
// The variables below affect the position of the objective mount
z_strut_l = big_stage?18:15; //length of struts supporting Z carriage
objective_mount_y = big_stage?18:12; // y position of clip for optics
objective_mount_nose_w = 6; // width of the pointy end of the mount
condenser_clip_w = 14; // width of the dovetail clip for the condenser
foot_height=feet_endstops?15:15; //the endstops need a bit of extra height (or not)

// These variables set the dimensions of flexures
// You might want to tweak them if your material (or printer)
// is different from the ones I've tested, though ABS/PLA extrusion
// is generally fine with my parameters
stage_flex_w = 4; // width of XY axis flexures
zflex_l = 1.5;    // length of (all) flexible bits
zflex_t = 0.75;   // thickness of (all) flexible bits
zflex = [stage_flex_w, zflex_l, zflex_t]; // the above in new-style format
flex_a = 0.15;    // sine of the angle through which flexures can be bent

// Compile a sensible version string
version_string = str("v",version_numstring, big_stage?"-LS":"-SS", sample_z, motor_lugs?"-M":"");
echo(str("Compiling OpenFlexure Microscope ",version_string));

stage_t=5; //thickness of the XY stage (at thickest point, most is 1mm less)
flex_z1 = 0;      // z position of lower flexures for XY axis
flex_z2 = sample_z-stage_t; //height of upper XY flexures
z_strut_t = 6;  // (z) thickness of struts for Z axis
z_flex_w = 4;   // width of struts for Z axis
leg = [4,stage_flex_w,flex_z2+zflex_t]; // size of vertical legs
leg_middle_w = 12; // width of the middle part of each leg
actuator_h = 25; //height of the actuator columns
dz = 0.5; //small increment in Z (~ 2 layers)

leg_outer_w = leg_middle_w + 2*zflex_l + 2*leg[0]; // overall width of parallelogram legs that support the stagef
actuator = [3*1.2+2*2,(flex_z2 - flex_z1)*xy_lever_ratio,6]; // dimensions of the core part of the actuating levers for X and Y - NB should match the column_base_r in compact_nut_seat.scad
actuating_nut_r = (flex_z2 - flex_z1)*xy_lever_ratio; // distance from leg_r to the actuating nut/screw for the XY axes
xy_actuator_travel = actuating_nut_r*0.15; // distance moved by XY axis actuators

// Z axis
z_flexures_z1 = 8; // height of the lower Z flexure
z_flexures_z2 = min(sample_z - 12, 35); // " upper "
objective_mount_back_y = objective_mount_y + 2; //back of objective mount
z_anchor_y = objective_mount_back_y + z_strut_l + 2*zflex[1]; // fixed end of the flexure-hinged lever that actuates the Z axis
z_anchor_w = 20; //width of the Z anchor
zll = (z_strut_l + zflex[1])*z_lever_ratio; //required actuator lever length
zfz = z_flexures_z1; // shorthand for the next line only!
z_nut_y = z_anchor_y - zflex[1]/2 + sqrt(zll*zll - zfz*zfz);
z_actuator_travel = zll*0.15; // distance moved by the Z actuator
z_actuator_tilt = -asin(z_flexures_z1/zll); //angle of the Z actuator

z_flexure_x = (leg_r-zflex_l-max(5,leg[2]*0.1))*sqrt(2); // x position of the outside of the Z-axis static anchors (either side of the XY stage, on the X axis) (no longer used by Z axis but still in use elsewhere.)

bridge_dz = 10; // spacing between thin links on legs
base_t=1; // thickness of the flat base of the structure
wall_h=15; // height of the stiffening vertical(ish) walls
wall_t=2; //thickness of the stiffening walls
zawall_h = z_flexures_z2 - 10; //height of wall near Z anchor
zbwall_h = z_flexures_z2 - 10; //height of bridge over Z lever
illumination_clip_y = (-(leg_r-zflex_l-wall_t/2+leg_outer_w/2)/sqrt(2)
                       -wall_t/2-1); //position of clip for
                      // illumination/back foot.  This is set to
                      // coincide with the wall between the back
                      // two legs. TODO: remove this
illumination_arm_screws = [[20,z_nut_y,sample_z-2],[-20,z_nut_y,sample_z-2], 
                           [0,(leg_r + leg_outer_w)/sqrt(2) + 4,sample_z-2]];
                      // positions of screws that mount the adjustable version of the 
                      // illumination arm
condenser_clip_y = -8; //position of dovetail for old condenser assembly TODO: rename this
base_mounting_holes = [[-20,z_nut_y-4,0],
                       [20,z_nut_y-4,0],
                       [-z_flexure_x-4,big_stage?-8:-4,0],
                       [z_flexure_x+4,big_stage?-8:-4,0]]; 
                       // holes to screw the microscope to a baseplate

endstop_extra_ringheight=feet_endstops?1:0;
endstop_hole_offset=0;
//this is a temporary option to printfeet with smaller travel
//without this with 15mm hole the stage hits the objective
//the stage can move ~3mm in each direction, so the actuator only moves
//~1.7 mm
avoid_objective_xyfoot_offset=xy_actuator_travel-1.8;

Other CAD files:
builds/microscope_stand_no_pi.stl
openscad/openflexure_emblem.dxf
stl/objective_mounting_test.stl
builds/slide_riser_LS10.stl
openscad/motor_driver_case.scad
builds/back_foot.stl
builds/camera_platform_picamera_2_LS65.stl
builds/condenser.stl
builds/feet.stl
builds/feet_tall.stl
builds/gears.stl
builds/illumination_dovetail.stl
builds/lens_spacer_picamera_2_pilens_LS65.stl
builds/lens_spacer_picamera_2_pilens_LS75.stl
builds/lens_tool.stl
builds/microscope_stand.stl
builds/microscope_stand_LS160.stl
builds/microscope_stand_LS20.stl
builds/microscope_stand_SS20.stl
builds/motor_driver_case.stl
builds/optics_logitech_c270_c270_lens_LS65.stl
builds/optics_logitech_c270_rms_f40d16_LS65.stl
builds/optics_logitech_c270_rms_f50d13_LS65.stl
builds/optics_m12_m12_lens_LS65.stl
builds/optics_m12_rms_f40d16_LS65.stl
builds/optics_m12_rms_f50d13_LS65.stl
builds/optics_picamera_2_pilens_LS65.stl
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

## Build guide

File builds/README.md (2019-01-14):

OpenFlexure Microscope: STL files
=================================

This folder contains the printable files you'll need in order to make an OpenFlexure microscope.  It is our intention that in the near future this folder will move to a proper build server, and stop cluttering up the repository.  It is important to note that **YOU SHOULD NOT JUST PRINT ALL THE FILES IN THIS FOLDER**.  Please read the printing instructions in the [documentation](../docs/) first.

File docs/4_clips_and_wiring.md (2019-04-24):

# Sample mounting and wiring

# Requirements
All the parts you need are shown below:

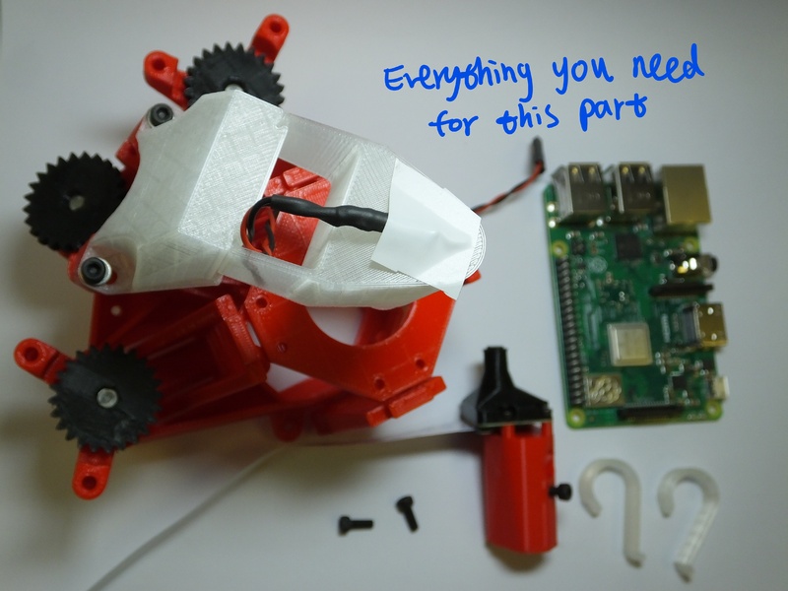
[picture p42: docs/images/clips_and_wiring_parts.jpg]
Parts needed for this section


## Parts
*   1 Microscope body, with 3 assembled actuators, an optics module, and the illumination attached.
*   2 [M3x8mm screws](./parts/m3x8mm_screws)
*   2 [Sample clips](./parts/sample_clips)
*   1 [Raspberry Pi](./parts/raspberry_pi)

## Tools
*   A 2.5mm ball-ended hex key

# Assembly Instructions
## Step 1
Plug the LED cable into the GPIO connector on the Raspberry Pi, to the 0v and 5v lines.  These are the second and third pins from the top of the connector, on the outside edge - pins number 4 and 6.

Plug in the camera to the camera connector as described in the [Raspberry Pi learning materials](https://projects.raspberrypi.org/en/projects/getting-started-with-picamera) (the connector is next to the Ethernet port, and the contacts on the cable face the port, i.e. they face away from the tab on the plug).
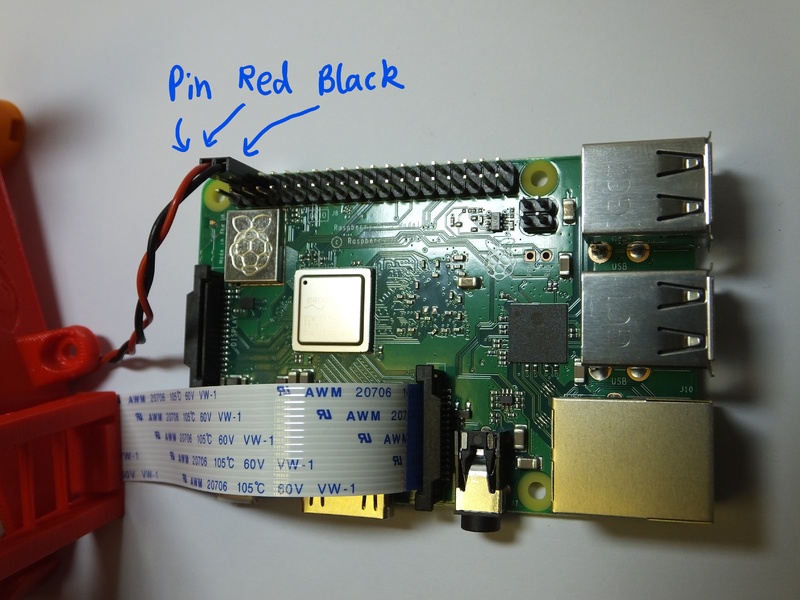
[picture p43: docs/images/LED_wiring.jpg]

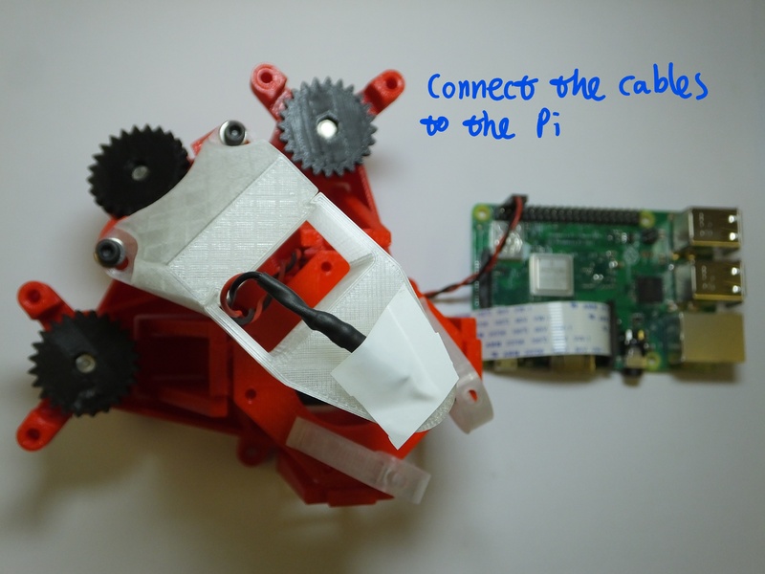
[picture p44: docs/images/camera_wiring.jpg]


## Step 2
If you are using a tall optics module, e.g. if you are using a plan corrected objective, you may need to fit a [sample riser](./parts/printed/sample_riser.md) between the microscope body and the microscope slide.  This is not necessary if you are using the basic optics module.

## Step 3
Fit the optics module onto the microscope - it slides in from the bottom as shown.  The screw sticking out the side fits into the "keyhole" shaped slot in the microscope body.
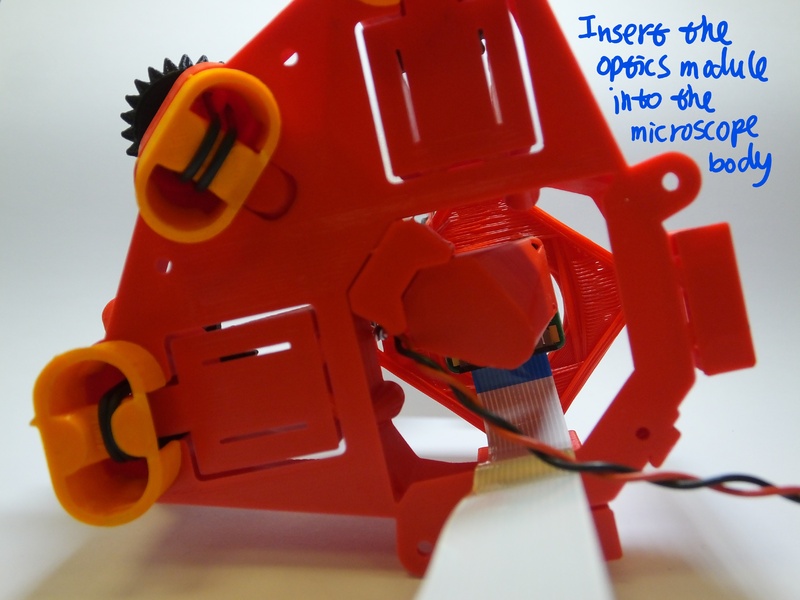
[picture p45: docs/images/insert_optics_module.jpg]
Insert the optics module


## Step 4
Tighten the screw to hold the optics module in place.  You can reach the screw with a ball-ended hex key, through the hole near the Z axis, as shown below:
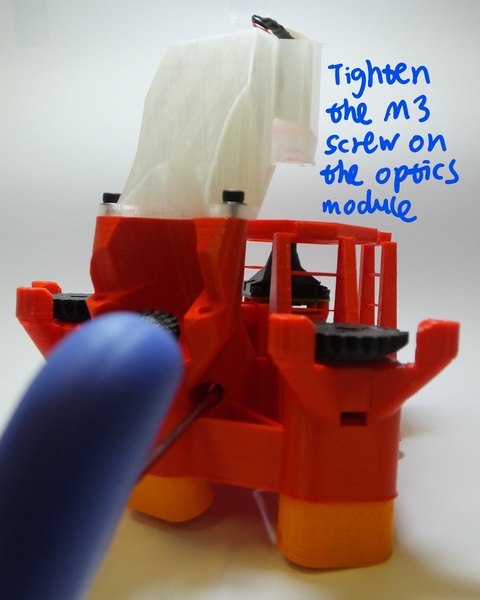
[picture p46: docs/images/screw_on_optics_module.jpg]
Tighten the screw to secure the optics module


## Step 3
After this, there are only the sample clips to go.  Exactly where you place these will depend on the samples you intend to use, but in any case you simply push the M3 screws into the clips, then screw down into the holes on the stage.
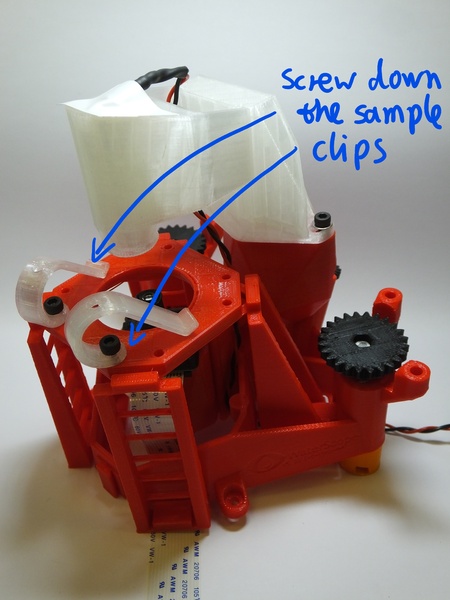
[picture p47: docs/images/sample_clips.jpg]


## Step 4
Your microscope is now complete - happy observing!
You might want to consult the [camera module documentation](http://www.raspberrypi.org/documentation/usage/camera/) or [raspicam documentation](http://www.raspberrypi.org/documentation/usage/camera/raspicam/README.md) if you need a hand setting up the camera.
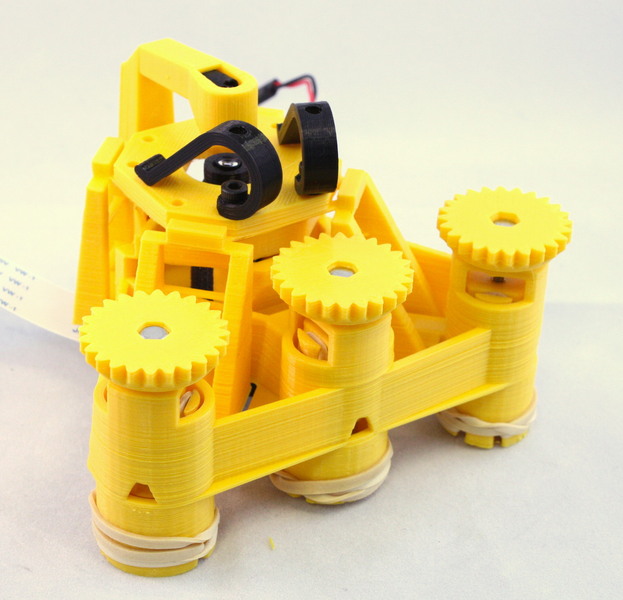
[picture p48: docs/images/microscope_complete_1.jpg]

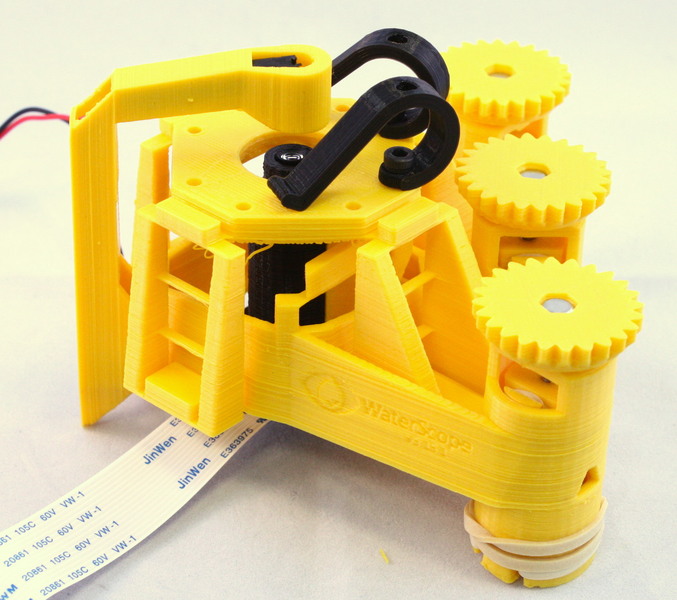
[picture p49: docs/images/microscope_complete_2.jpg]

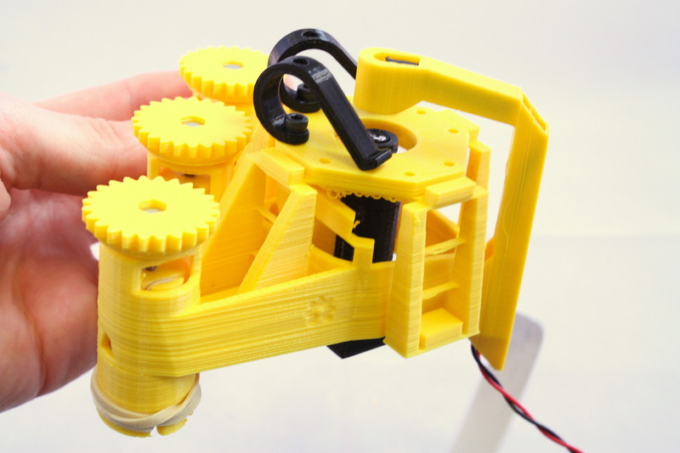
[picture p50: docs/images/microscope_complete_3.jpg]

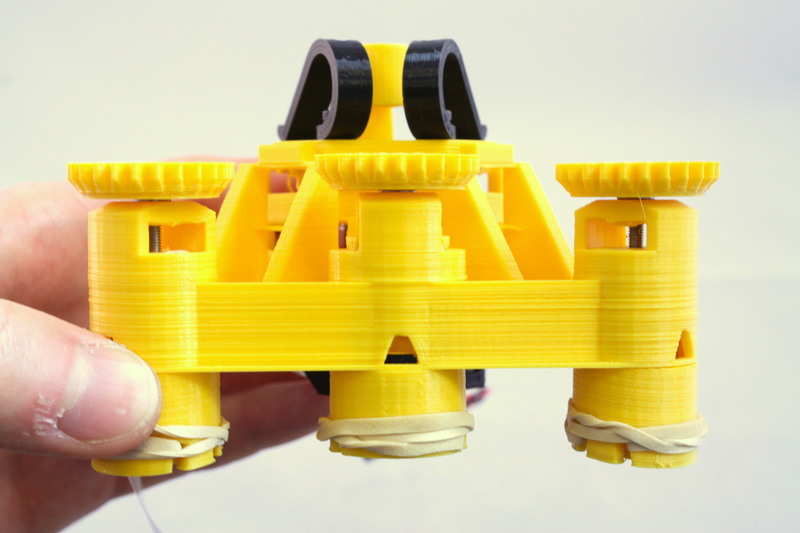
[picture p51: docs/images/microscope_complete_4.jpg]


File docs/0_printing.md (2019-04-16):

# Printing the plastic parts
First, you will need to print or obtain the 3D printed parts.  These have been designed with some care to print reliably on most RepRap-style printers, without support material.  It's important to read through the notes before, as there are multiple versions of the STL files to choose from, so it's not a good idea just to pick all the parts in the folder.

## Print settings
I usually print with a layer size of 0.24mm on my Ormerod, which takes 10 hours for the main body.  "low" quality on an Ultimaker 2 (0.15mm layers) produces similar results in about 10 hours.  Our Prusa i3 Mk3 takes a similar time using 0.2mm layers, or 0.3mm layers if we want to go even faster (8 hours or less).

> **Warning:** The microscope is designed to print without support material.  If you use support material it will require a lot of cleaning up, and you may well damage the parts.

The parts are all designed to print without support material or adhesion layer.  If you do use an adhesion layer, many of the moving parts will be rendered useless by a brim (particularly on the main body), and require lots of work with a craft knife to sort them out.  While there are no cantilevered parts that really need support, there are a few bridges; it might be a good idea to print the ``just_leg_test.stl`` file first, to make sure your printer can print them.  There are some versions of the main body that include a baked-in brim in the STL file, see [``main_body.scad``](../openscad/main_body.scad).  This brim does a better job of not fouling the mechanism than most slicers, and is a good option if the part won't stick without a brim.  Most of the other parts are possible to clean up after printing with a brim, so you may wish to use one, particularly for the smaller parts like sample clips.

If your printer has a standard-sized bed (180mmx180mm should be fine) then it should be possible to print the complete microscope in one go.  I do this if I'm using a machine that is well calibrated and reliable.  However, I find that it's often more reliable to print in batches (as small parts at the edge of the print bed can detach and cause it to fail).  I would recommend: 

*   Batch 1: Microscope, illumination and Optics module (this is the longer print, with taller objects)
*   Batch 2: Feet, gears, camera cover, camera board gripper, camera lens remover, gear riser

There is a test file that prints a single leg of the microscope - ``just_leg_test.stl``. It's worth printing this first to check your settings are OK.

The optics module needs to print with some fine detail, so the dovetail meshes nicely with the stage.  A good way to ensure this is to print it at the same time as other parts - either print more than one optics module at a time, or print it at the same time as the microscope body.  This slows down the time for each layer, and means the plastic can cool more completely before the layer on top is deposited, resulting in a higher-quality part.  The optics module is best printed in black to cut down on stray light inside the tube - though it will still work in other colours.

## Standard builds of the microscope
The list of parts below is pretty extensive and tries to explain all the various options - however, if you just want to build a "normal" version of the microscope, there are two versions we'd reccommend:

### Webcam-based microscope
The basic version of the microscope uses a webcam lens instead of a microscope objective - you still get a really nice focusing/sample translation stage, but with basic options.  This version is great for school or hobby use, gets a resolution of about 2um or better, and is the cheapest to build.  This is the version we usually build at workshops.  For each microscope, you will need to print one copy of each of the following files:

* ``actuator_assembly_tools.stl``
* ``picamera_2_gripper.stl``
* [optional] ``picamera_2_lens_gripper.stl`` (only needed if your camera didn't come with a tool to remove the lens) 
* ``main_body_LS65.stl``.
* ``feet.stl``
* ``gears.stl``
* ``illumination_dovetail.stl``
* ``condenser.stl``
* ``sample_clips.stl``
* ``camera_platform_picamera_2_LS65.stl``
* ``lens_spacer_picamera_2_pilens_LS65.stl``
* ``microscope_stand.stl`` or ``back_foot.stl``

This will need the nuts, bolts, etc. described below, plus a Raspberry Pi computer (any model will do) and Raspberry Pi camera module.  No other optical bits are required, except an LED for illumination.  If your Raspberry Pi is in a case already, you should print ``back_foot.stl`` so the microscope sits flat on a table.  If you want to mount the Raspberry Pi underneath the microscope (our preferred option), print ``microscope_stand.stl`` instead.  Newer camera modules include a white circular tool for unscrewing the lens.  If you don't have one, you will need to print the lens gripper (marked as optional).

### High resolution microscope
The version of the microscope used for scientific or medical research generally requires a conventional objective lens.  Most of the parts are the same, but the optics and sample mount are different.  You will need one copy of each of the following files:

* ``actuator_assembly_tools.stl``
* ``lens_tool.stl``
* ``picamera_2_gripper.stl``
* [optional] ``picamera_2_lens_gripper.stl`` (only needed if your camera didn't come with a tool to remove the lens) 
* ``main_body_LS65-M.stl``.
* ``feet.stl``
* ``gears.stl``
* ``illumination_dovetail.stl``
* ``condenser.stl``
* ``sample_clips.stl``
* ``optics_picamera_2_rms_f50d13_LS65.stl``
* ``microscope_stand.stl``
* ``sample_riser_LS10.stl`` (assuming you have a microscope objective with a 45mm parfocal distance)

**For motorised operation you will also need**
* ``small_gears.stl``
* ``motor_driver_case.stl``

Additionally, you will need:
* an RMS threaded, finite-conjugates objective lens.  These can be obtained from e.g. AliExpress.  Depending on whether it is 35mm or 45mm from the "shoulder" of the lens to the sample, you may or may not need the sample riser.  We almost always use 45mm "plan" corrected lenses, which do require the riser.
* a 12.7mm diameter, 50mm focal length achromatic lens, e.g. ThorLabs ac127-050-a or generic equivalent.
* a 13mm diameter, 5mm focal length PMMA lens for the condenser (sold as LED lenses in bulk)
* three 28BYJ-48 stepper motors and a [sangaboard](https://github.com/rwb27/openflexure_nano_motor_controller/) driver, or other suitable electronics.

## Required parts
Make sure you have all the necessary parts and tools.  The parts should all be listed in the bill of materials, which is currently a work in progress (eventually it will be produced automatically, which should help it to stay accurate).  We reccommend reading through all the instructions, rather than trusting what is currently listed here. 

### Printed parts
Currently, the STL files live in the [builds folder](../builds).  This will move to a build server soon.

**Plastic tools:**
* band and nut insertion tools ``actuator_assembly_tools.stl``
* tool to insert the 13mm diameter condenser lens and/or tube lens: ``lens_tool.stl``
* jig to hold the camera board while you unscrew the lens ``picamera_2_gripper.stl``
* [optional] tool to unscrew the camera's lens (only needed if your camera didn't come with one) ``picamera_2_lens_gripper.stl``

**Components:**
* body of the microscope: ``main_body_<stage size><height>[-M].stl``.
* 3 feet: ``feet.stl`` or ``feet_tall.stl`` (contains all 3)
* 3 large gears: ``gears.stl`` (contains all 3)
* illumination:
 - ``illumination_dovetail.stl``
 - ``condenser.stl``
* 2 sample clips: ``sample_clips.stl`` (contains both)
* optics module (you need one of the two options below):
 - old-style optics module (one part, best with RMS objectives): ``optics_<camera>_<lens>_<stage size><height>.stl``
 - platform-style optics module (two parts, best with webcam lenses): ``camera_platform_<camera>_<stage size><height>.stl`` and ``lens_spacer_<camera>_<lens>_<stage_size><height>.stl``
* [optional] camera cover: ``picamera_2_cover.stl``
* [optional] 3 small gears for motors: ``small_gears.stl`` (contains all 3)
* [optional] riser for the sample: ``sample_riser_<stage size><thickness>.stl``
* [optional] slide holder that works better if using immersion oil: ``slide_riser_LS10.stl``
* [optional] base to hold a Raspberry Pi: ``microscope_stand.stl``
* [optional] base to hold the motor driver (fits under the base that holds the Pi): ``motor_driver_case.stl``
* [optional] back foot, in case you are not using the microscope stand: ``back_foot.stl``

In the filenames above, where there are multiple versions, parameters are included in angle brackets:
* ``<stage size>`` selects the size of the platform - but currently only ``LS`` is supported.
* ``<height>`` is the height from the bottom of the main body to the top of the stage in mm, currently either ``65`` or ``75``. 
* Usually the above two parameters occur next to each other, so you will see ``LS65``.  I pretty much only use ``65`` as standard, and if I am using an objective (which is the norm) I add a 10mm riser.
* ``<camera>`` is the camera you are using, either ``picamera_2`` for the Raspberry Pi camera module v2, ``c270`` for the Logitech C270, or ``m12`` for a camera with a screw-on M12 lens mount.
* ``<lens>`` is the lens you are using, either ``pilens``, ``c270_lens``, or ``m12_lens`` if you are using the lens that came with your camera.  To use a finite-conjugate, RMS threaded objective lens, you should specify ``rms_f50d13`` (for a 50mm focal length, 12.7mm diameter tube lens, e.g. ThorLabs ac127-050-a).  You can also specify ``rms_f40d16`` (to use a Comar tube lens, focal length 40mm, diameter 16mm) but this is deprecated as the images weren't as good. 
* ``<thickness>`` is the thickness of a stage riser - the amount it adds to the height.  Usually a 10mm riser is used with a 65mm body to allow a 45mm parfocal distance objective to be used, currently only LS10 is reccommended.
Optional bits of filenames are in square brackets above:
* ``-M`` in the body name means it has motor lugs to allow 28BYJ-48 stepper motors to be fitted
* ``_tall`` on the illumination or the feet means the body sits 26mm off the ground rather than 15mm, to give clearance for larger camera modules.  This is only useful if you are not using the microscope stand.

Currently, there are two reccommended versions of the body; ``LS65`` and ``LS65-M``.  The only difference is that the ``-M`` version can be fitted with motors.  To build the high-resolution version of the microscope, use the 10mm thick sample riser ``sample_riser_LS10.stl``, and ``optics_picamera_2_rms_f50d13_LS65.stl``.  To build the low-resolution version, don't use the sample riser, and instead use ``camera_platform_picamera_2_LS65.stl`` and ``lens_spacer_picamera_2_pilens_LS65.stl``.  In both cases, it's best to print the microscope stand, and use the standard-height feet.

## Clean-up of printed parts
If you printed the parts yourself, start by opening out the three holes in the microscope body with a drill as shown.  Make sure to go all the way through.  If you don't have a drill, you can improvise by screwing in an M3 screw all the way, then forcibly rotating it with a screwdriver or the supplied nut.  Also, remove any loose strings of plastic from the underside of the sample stage, using a pair of pliers. The last step shouldn't be necessary if your machine is calibrated nicely for printing bridges.

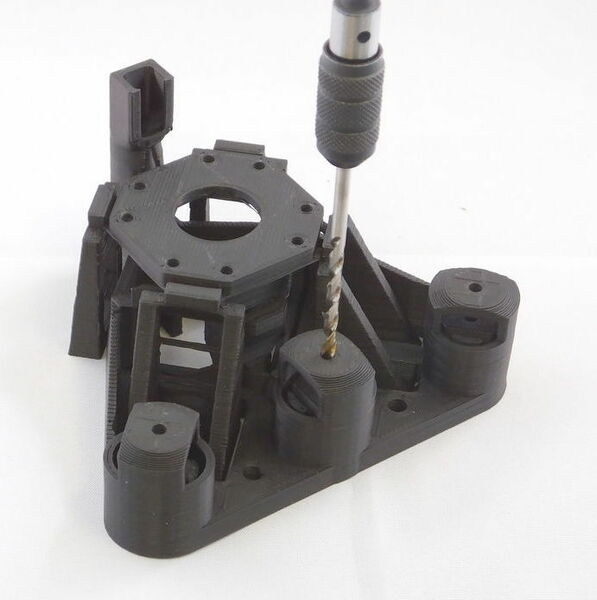
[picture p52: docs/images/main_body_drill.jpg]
Opening out the holes for the actuators


There are also ties between the actuator column casing and the central actuator column that holds the brass nut - these need to be snapped, as described in the instructions later on.  There may also be short ties between the two thinner pairs of legs and the "wall" running around the microscope - these should also be snapped with a knife.  The "ladder" like structure between each pair of legs is also only there for support during printing - it does no harm to leave it in place, but if you cut the "rungs" out, it will allow the stage to move a little more freely.

Once you have your printed parts, you can start by [assembling the actuators](./1_actuator_assembly.md).

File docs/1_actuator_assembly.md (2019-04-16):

# Actuator assembly
There is one "actuator column" for each of the three axes of the OpenFlexure Microscope stage, to allow you to move the sample in X and Y, or focus the microscope by moving in Z.  It consists of a plastic gear that fits onto an M3 screw, which then pulls up on a brass nut.  Elastic bands pull down on the nut, tensioning the system.  The elastic band tightens up the mechanism, allowing us to move up and down smoothly.  Without the elastic band, you will only be able to move in one half of the microscope's range of travel, and the mechanism will be more wobbly.

# Requirements
All the parts you need for this step are in the picture below:

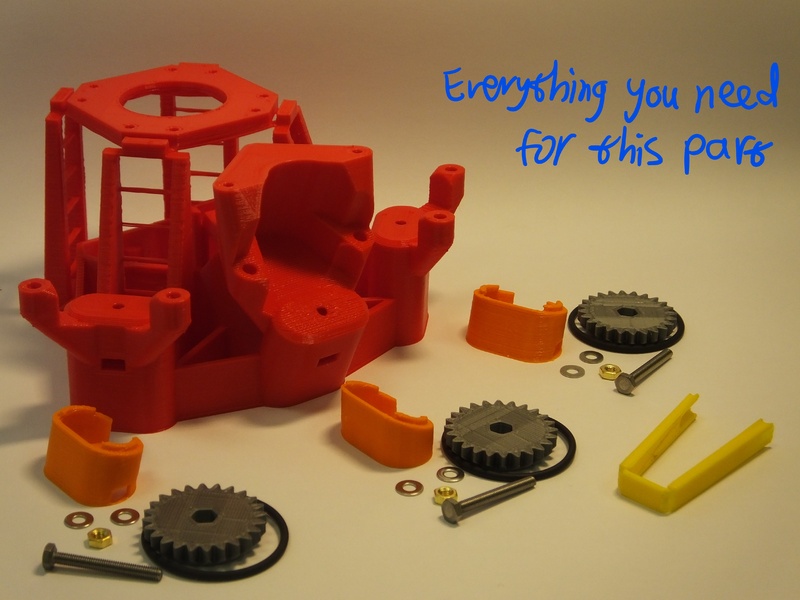
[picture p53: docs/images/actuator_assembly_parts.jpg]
Parts required for this step


## Parts
*   3x [M3x25mm hexagon head screws](./parts/fixings/m3x25mm_hexagonhead_screw.md), stainless steel
*   3x [M3 brass nut](./parts/fixings/m3_brass_nut.md)
*   6x [M3 stainless steel washers](./parts/fixings/m3_washer.md)
*   3x [Viton O-ring, 30x2mm](./parts/fixings/viton_o_ring_30mm_inner_diameter_2mm_cross_section.md) (NB: get some spares!)
*   3 [Plastic gears](./parts/gearthumbscrew)
*   1 set of [Microscope Feet](./parts/microscope_feet) (NB there are different feet for X/Y axes and for the Z axis).
*   light grease (if available)

## Tools
*   [Nut insertion tool](./parts/nut_insertion_tool)
*   [O ring insertion tool](./parts/o_ring_insertion_tool)
*   [Craft knife](./parts/craft_knife)

# Assembly Instructions
There are three actuator columns on the microscope, for X, Y, and Z.  Follow these instructions for each column in turn.

## Step 1
We need to place a nut inside the actuator.  Insert it from the side, through the slot in the actuator column, and push it into place with the [nut insertion tool](./parts/nut_insertion_tool).  Take care to insert the nut corner-first (i.e. with flat sides parallel to the tool), otherwise it will jam.

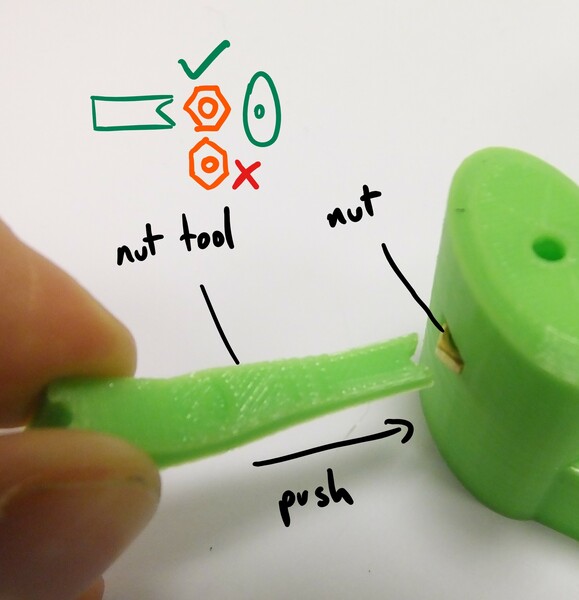
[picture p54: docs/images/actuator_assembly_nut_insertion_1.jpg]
putting the nut into the actuator column

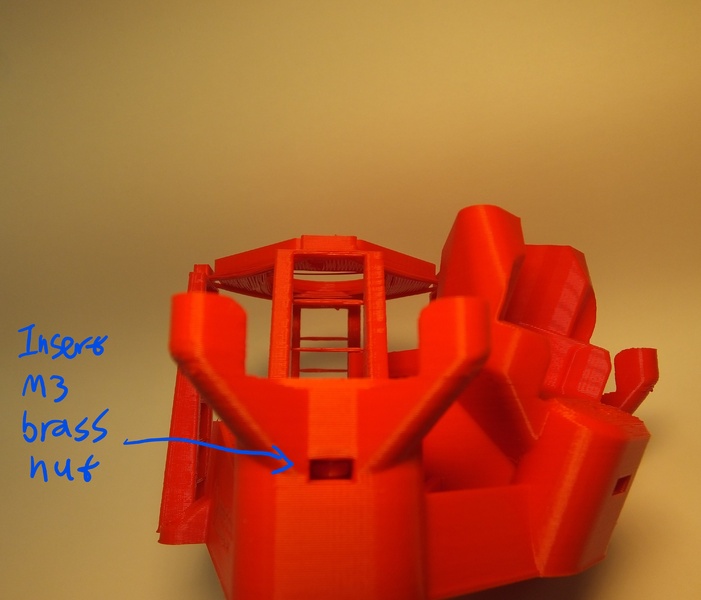
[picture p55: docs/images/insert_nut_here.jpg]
The slot in the body now looks like this


## Step 2
Next, take a screw, and push it into a plastic gear, so that the head of the screw is embedded in the plastic.  Then, thread two washers onto the screw where it sticks out of the gear.  Put a very small blob of light oil or grease (if available) on the screw thread.  Put the screw into the hole at the top of the column, and screw it into the nut that is now inside the actuator.  The two washers should sit between the gear and the microscope body

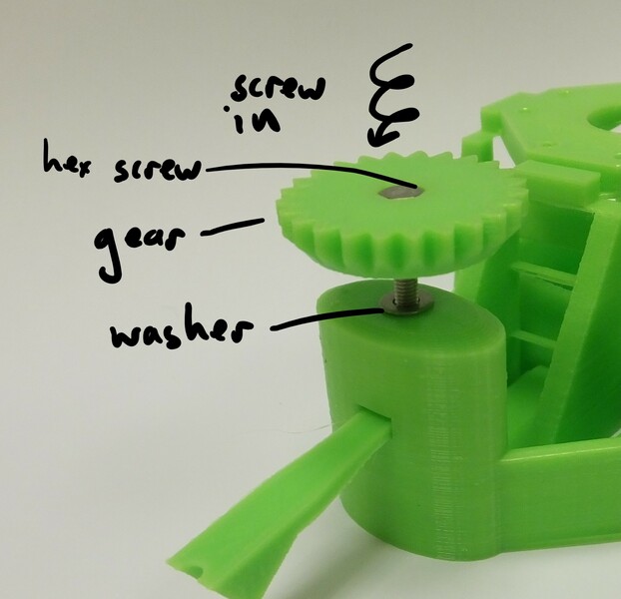
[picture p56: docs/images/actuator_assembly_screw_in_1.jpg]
assembling the screw into the actuator column

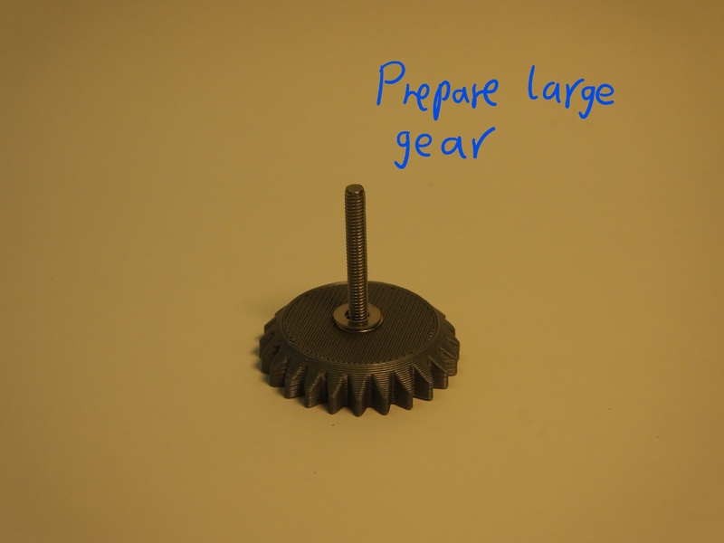
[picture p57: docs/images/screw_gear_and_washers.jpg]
The gear, with the screw and washers in place


## Step 3
Turn the microscope over and, using the elastic band tool or a craft knife, snap the two thin plastic supports as shown if they are present.
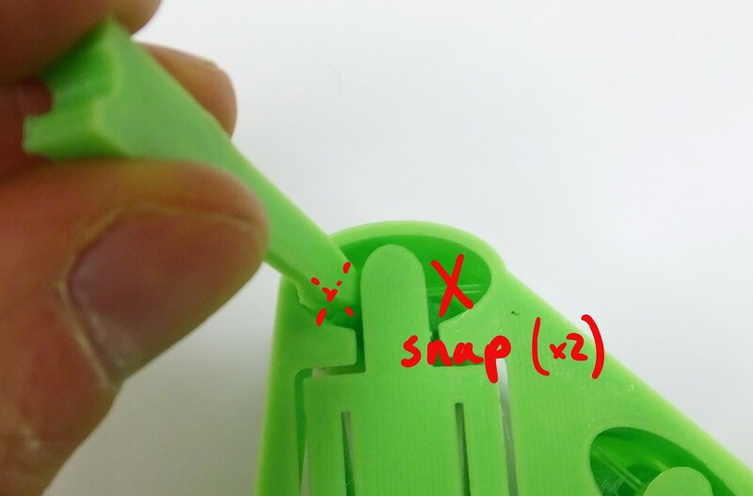
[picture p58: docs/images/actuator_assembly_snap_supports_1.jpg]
removing the ties that support the actuator column during printing


## Step 4
Hook one of the Viton bands over the elastic band tool, and pass the tool through the foot as shown.  You should end up with one loop of elastic band passing over each fork-shaped end of the insertion tool.  The flat side of the tool should be on the outside, so that the channels in either end face towards the centre of the foot.  Make sure you pick the right foot - the middle axis (Z) has a smaller foot.  The angle of the feet is different, if the foot doesn't line up with the outside of the microscope casing, you may be using the wrong one.

You may find it easier to put the band through the foot, then insert the tool and hook the band over either end - either way you should end up with the band, foot, and tool arranged as shown in the pictures.

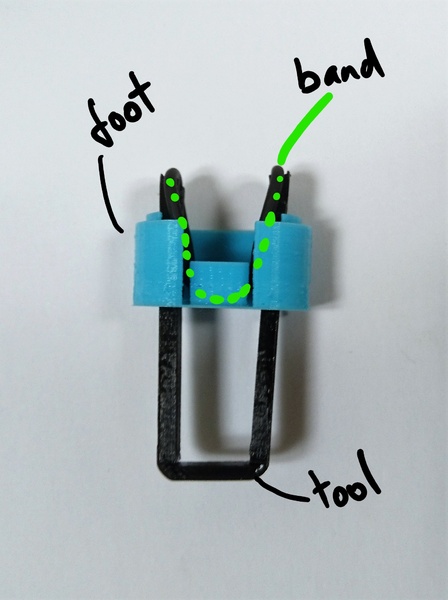
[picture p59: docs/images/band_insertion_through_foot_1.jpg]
The elastic band on the insertion tool, passed through the foot

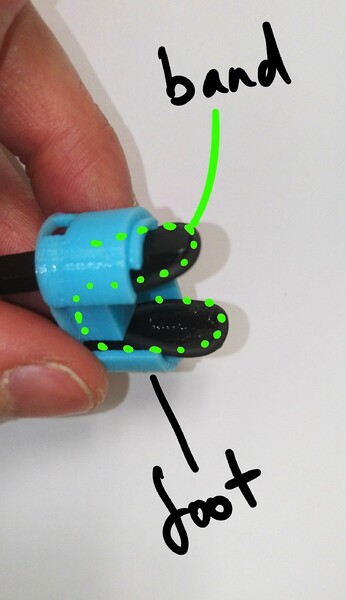
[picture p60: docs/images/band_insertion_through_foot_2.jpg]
Inserting the elastic bands


## Step 5
Place the foot on the body, taking care that it's in the right place (the outer two actuators have sloping bottoms, but flat tops, the central Z axis has a sloping top and a flat bottom). You must also take care to put them on the right way round; the open part of the foot points towards the optics module in the centre of the microscope.

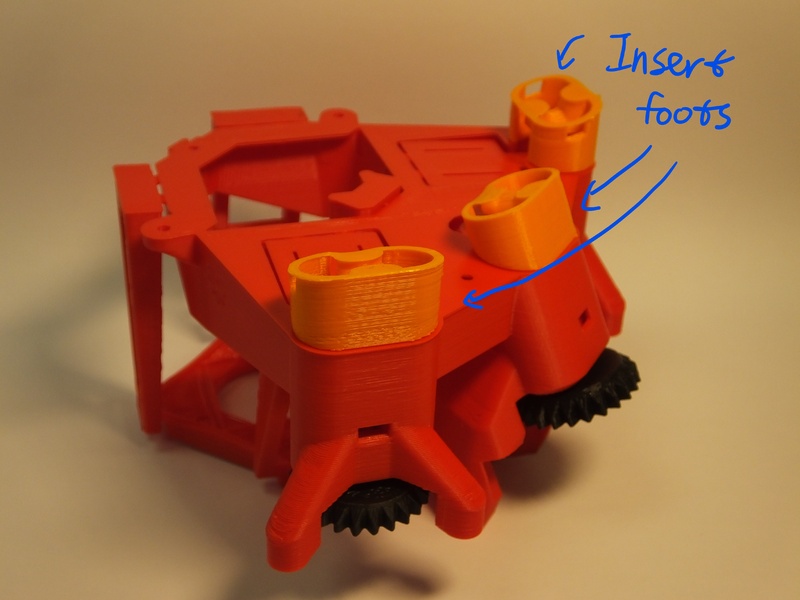
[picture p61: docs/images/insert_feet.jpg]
Feet fitted into the microscope

 
Push the insertion tool in until the band clicks into place.  Use the nut insertion tool to hold the actuator in place while you do this.  It might help to unscrew the gear a bit (so you can see some of the screw thread between the body and the gear) and push down on the gear.  When you push the band in, it should click twice - once for each side.  If you don't manage to hook both sides on, you may need to completely remove the band and try again - a wooden skewer, or small flat-bladed screwdriver works well to unhook the band without damaging it.
 
What's happening here is that the elastic band is pushed over little hooks inside the actuator column, near the top, and the click is the band popping into place.  The band pulls down on the actuator, so after it's in place the gear should turn with a little more resistance - this is important for the microscope to work properly.

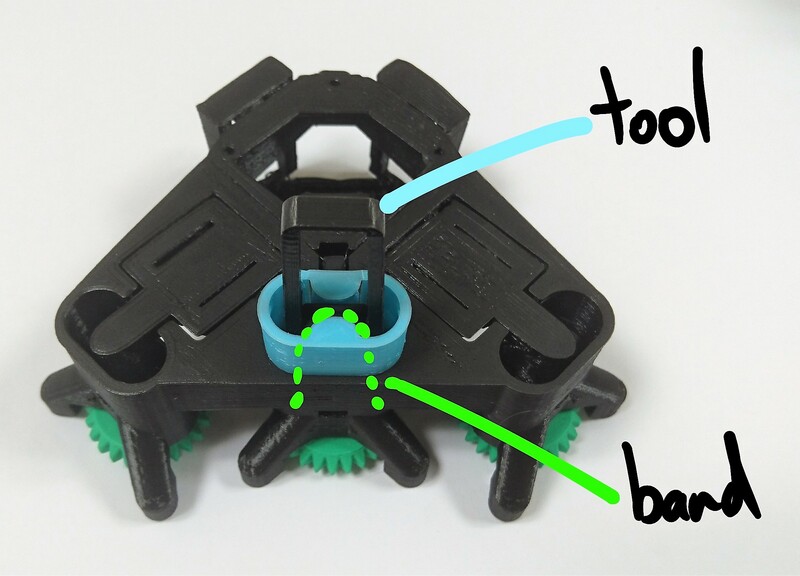
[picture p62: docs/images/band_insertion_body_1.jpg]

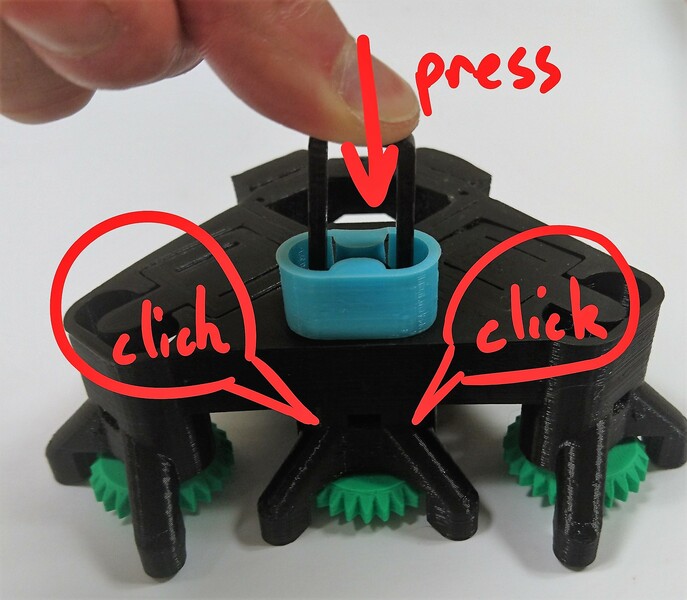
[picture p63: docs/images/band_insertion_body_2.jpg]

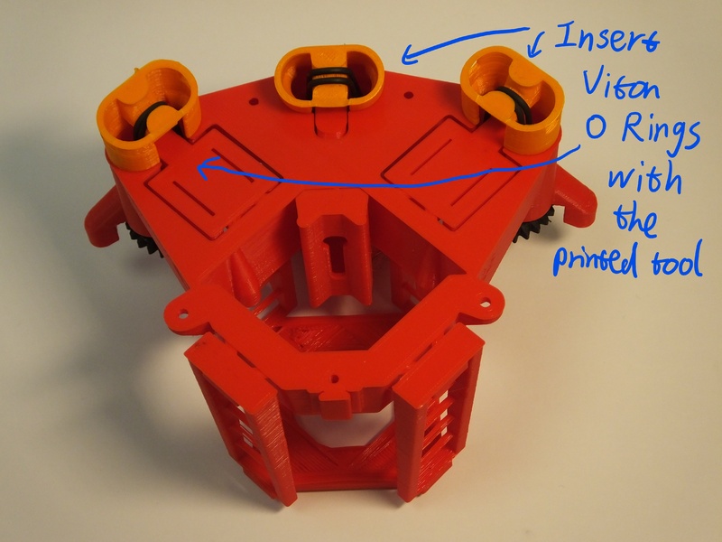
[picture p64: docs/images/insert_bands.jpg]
The bands and feet in place in the microscope body


## Step 6
You should now have the band pulling both sides of the actuator down as shown.
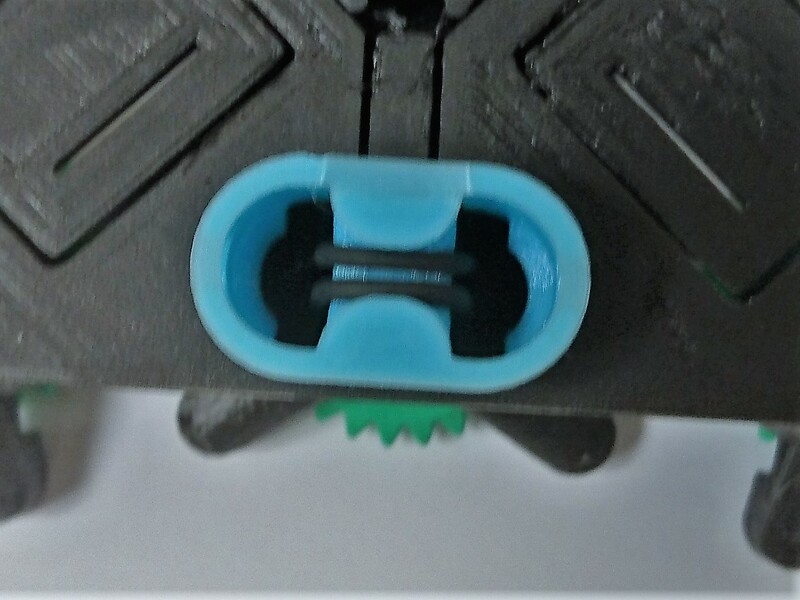
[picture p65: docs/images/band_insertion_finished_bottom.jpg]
The Viton o ring, in place in the microscope's foot.


## Step 7
Congratulations, you've assembled the actuator!  There are three to do, so you may now need to go back and make the next one.

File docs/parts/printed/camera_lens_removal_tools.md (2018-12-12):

# Camera lens removal tools
Camera lens removal tools

## Details
*   **Material used:** 0.01
*   **Material units:** KG

## Media
*   
*   
*   

# Manufacturing Instructions
## Step
These tools make it much easier to remove the lens from a Raspberry Pi camera module.  See the documentation for the Raspberry Pi Camera Mount/Extension Tube for instructions.  These tools are for version 2 of the camera board.  The board gripper for v1 is included for convenience - you'll need a small pair of pliers (I like mini combination pliers) to unscrew the lens if you have v1 of the board.  v2 of the Raspberry Pi camera module now comes with a lens removal tool, which is better than the printed one - but the board gripper is still useful.

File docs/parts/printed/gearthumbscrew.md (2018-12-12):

# Gear/thumbscrew
Gear/thumbscrew

## Details
*   **Material used:** 0.01
*   **Material units:** KG

## Media
*   

# Manufacturing Instructions
## Step
These gears are used to control the leadscrews that move the stage.  You can replace them with more comfortable thumbscrews if desired, or use stepper motors to drive them automatically.  You need three gears.  NB the gears are designed to print with the circular face down, this avoids marring of the teeth and helps it stick to the bed better.

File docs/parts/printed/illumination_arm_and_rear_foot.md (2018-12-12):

# Illumination arm and rear foot
Illumination arm and rear foot

## Details
*   **Material used:** 0.01
*   **Material units:** KG

## Media
*   
*   
*   
*   
*   

# Manufacturing Instructions
## Step

The illumination arm fits on to the microscope using a dovetail, and includes the rear foot.  The condenser lens version will also work without a lens, though the image won't be as bright.

The illumination arm is available in several versions: `illumination_and_rear_foot_[version].stl`.  You can choose either adjustable arm with a single LED or one that uses a condenser lens (`_condenser`).  It's important to match the type of microscope you're using (`LS65`, `LS75`, or `SS40`).  If you are using a riser to make space for a larger objective (if you've got a 35mm parfocal length objective) you'll need the `LS75` version.  If you are using tall feet, you will need the `_tall` version.

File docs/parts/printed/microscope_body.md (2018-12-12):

# Microscope Body
Microscope Body

## Details
*   **Material used:** 0.1
*   **Material units:** KG

## Media
*   
*   
*   
*   

# Manufacturing Instructions
## Step
This should be printed without support material.  On smaller/less well calibrated machines, I print this part on its own and then print the rest of the parts in a second print.  Which version of the body you need depends on two things: firstly, whether you want to use a large optics module (versions with LS65 in the name) or a small one (versions with SS), and secondly whether you want attachment lugs for motors (files with -M in the name).  All the files start with `body_`.You need the SS version if you're using a Raspberry Pi camera or a Logitech C270 camera, together with the lens that came on the camera.  If you're using a microscope objective, or the USB camera with M12 lens, you need the LS65 version.  The microscope body takes around 8 hours on a RepRapPro Ormerod (and many other low-end printers) or about 5 hours on Ultimaker, MakerBot, and the like. 
### Media
*   

## Step
After printing, you should run a 3mm drill bit through the 3mm holes in each actuator, to ensure the screws can rotate freely.  If you don't have a drill, an M3 screw should do...
### Media
*   

## Step
If the bottom layer has oozed out too much, or if you used a brim (not reccommended) you might need to clean up the bottom so it looks like this - it's important that the moving parts aren't stuck to the body with a thin layer of plastic (this most often happens around the struts connecting the objective clip to the rest of the microscope).
### Media
*   

## Step
You may need to use needle-nose pliers to pull strings of plastic from the underside of the microscope stage or the underside of the caps of the actuator columns.  If your printer is correctly calibrated there shouldn't be much, and I often get away without any - but some printers (particularly if using ABS) are prone to a bit of "spaghetti" under the stage.

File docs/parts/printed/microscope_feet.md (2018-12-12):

# Microscope feet
Microscope feet

## Details
*   **Material used:** 0.01
*   **Material units:** KG

## Media
*   

# Manufacturing Instructions
## Step
You need two tilted feet and one untilted foot, as provided in feet.stl.

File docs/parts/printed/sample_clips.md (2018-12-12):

# Sample Clips
Sample Clips

## Details
*   **Material used:** 0.002
*   **Material units:** KG

## Media
*   

# Manufacturing Instructions
## Step
These are optional, but they are useful for holding slides on the stage.  Usually, I use two of these for a normal microscope slide, screwed onto the top of the stage.

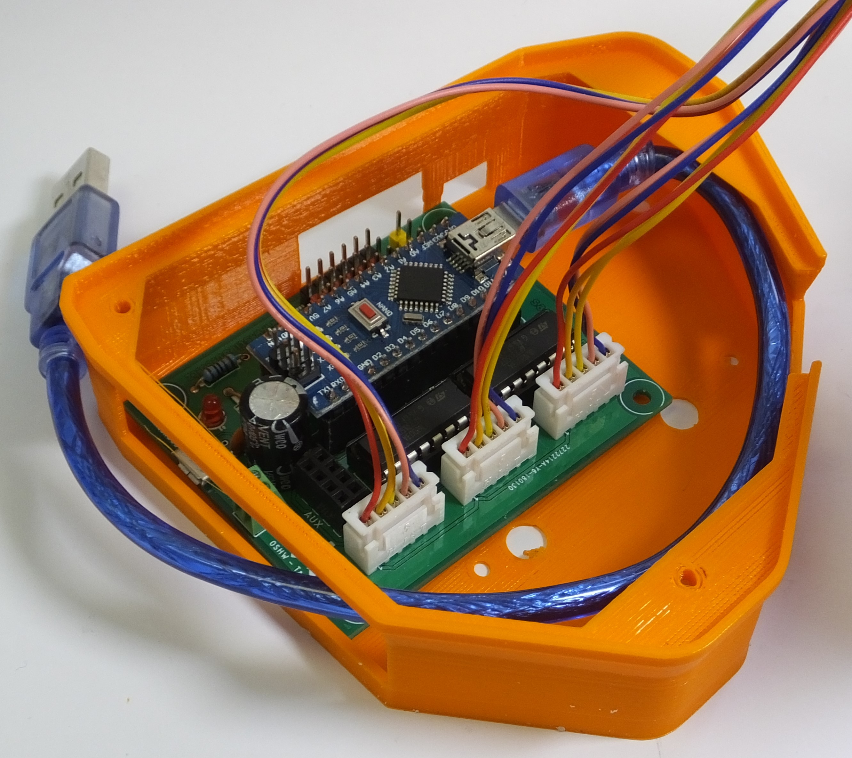
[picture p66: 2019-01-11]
docs/original_images/motors_wiring.jpg

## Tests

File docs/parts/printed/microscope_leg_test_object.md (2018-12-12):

# Microscope leg test object
Microscope leg test object

## Details
*   **Material used:** 0.01
*   **Material units:** KG

## Media
*   

# Manufacturing Instructions
## Step
This test piece checks your printer can bridge between the tops of the legs without failing.  If it passes this test, you're probably fine to print the rest of the microscope.

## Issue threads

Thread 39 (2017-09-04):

### ISSUE TITLE
Utilities issue

### ISSUE THREAD

**Issue by GraceAnyelwisye** [rwb27/openflexure_microscope#39]
1.What is the use of utilities? Why in almost all objects/parts you have included utilities? What is the relationship with the design? In some other parts, when I comment out utilities there is no significant change that I can observe. 

2. What does trylinder, shaft and delta mean in utilities?

**Comment by rwb27** [comment]
Hello
``utilities.scad`` contains a lot of useful functions, which are used in pretty much all the other files.  It doesn't create anything on its own, but it defines things like for example ``reflect(axis)`` which duplicates an object by reflecting it along a given axis.  It's like ``mirror`` only it keeps the original object.  While it's possible that some of the files don't actually need it, I tend to leave it in just in case.

"trylinder" generally refers to a shape that is somewhere between a triangle and a cylinder.  It's used in the lens grippers in the optics module (it is a shape that deforms to be a cylinder).

"shaft" is often used in connection to holes for screws/nuts - if "shaft=true" is specified, it will make a long hole for the shaft (threaded part) of the screw rather than just a hexagonal hole for the nut.

"delta" is used in the ``repeat`` module, and it sets the distance between the copies of the objects (it's a 3-element vector).

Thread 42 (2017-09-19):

rwb27/openflexure_microscope #42: Support for $3 chinese webcams

rwb27, 2017-09-19:
The cheap webcams used by e.g. [hackteria](https://hackteria.org/wiki/DIY_microscopy) would be a nice alternative for educational stuff, particularly when working in areas of the world where the £25 price tag of a Raspberry Pi camera or Logitech C270 is a problem.

rwb27, 2017-09-19:
I've tested out one of these - it works OK, and the lens was mounted in an M12 thread so I could actually use the same optics module as I use for the WaterScope chinese webcam.  I de-soldered the LEDs from the board, and had intended to use one of them for illumination - but they all seem to have stopped working...

The main issue is that, with the ~50mm tube length of the M12 optics module, the image is massively too zoomed-in.  What would be ideal is to come up with a module that places the sensor right next to the lens, which would get a zoomed-out image with similar resolution.  That would not only look better, it would also be more useful for education, where a slightly lower magnification is often desirable.

This might require making the stage a bit bigger to fit the board inside the stage rather than underneath the microscope, as it is currently.  I'm imagining a dummy optics module that finishes in a platform, the board sitting on that platform, and the lens mounted directly on top of the camera PCB.

rwb27, 2017-09-19:
@matthewlippincott do yell as and when you might be interested in this.

rwb27, 2017-10-04:
I sketched out what the mount I'm suggesting would need to do:
[image]
The lens can just be unscrewed and taped upside down to the holder on the PCB.  We'd then just need a platform that holds the camera, mounted on the dovetail.

rwb27, 2017-10-11:
I've made a start on this in the [6led_webcam](https://github.com/rwb27/openflexure_microscope/tree/6led_webcam) branch.  It's just a flat platform and needs blu tac/other mounting technology - something that clips or screws onto the camera board would be much better!

Maaphoo, 2018-01-25:
Recently I've been working on the 6 LED webcam version and a few other items. I've done the following:

- Made a Solidworks version of the microscope. I know it isn't in the open source tool chain, but it has helped me (I can't say I have an OpenSCAD brain).
- Modified the actuator columns so that they no longer require o-rings or rubber bands. Instead they have nylock nut, that keeps the thumbwheel in place. The nut in the actuator column is also more firmly anchored. 
- Added stops inside the actuator housing to limit the downward motion of the actuator columns to compensate for the fact that there are no longer feet.
- switched the illumination to something similar to what is being used by  hackteria.
- created an optics holder that fits onto a modified objective clip.
- Increased the size of the stage for the 40mm version so that the optics can fit.

**Issues I'm having:**
- There isn't much space for the modified objective clip and it can be difficult to assemble. I'm still working on getting the files adjusted so they fit together without post prossing.
- For some reason, the optics don't align vertically when they are attached. This has caused some motion in the y direction during focusing. I may have to angle the objective clip to get things to line up.

I can send STEP, STL or Solidworks files if they are of interest.

Here are some pics:

[image]
Cheek cells using the 6 LED webcam. The LEDs that come with the cam give quite a blue tint. Might be worth a few more cents to find something a bit whiter.

[image]
Just screwed onto a board with spacers in between. In Nairobi we use basically the same thing, but nicer and with a cover. 

[image]
View of how the illumination attaches. Just tapped into 2 of the led pads on the pcb. I'll use black heat shrink to cover next time instead of the blue electrical tape.

[image]
Here you can see the nylock nut and the lead screw nut in the nut trap below. Also notice that the actuator on the left is at it's max position, stopped by the limiter inside of the column.

rwb27, 2018-01-26:
Nice work @Maaphoo!  I would **love** to see your CAD files, I guess you can upload them to this issue or point me to a github repo somewhere.  Sounds like you've done a power of work and your images look fab.  STLs and Solidworks would be great, I don't have Solidworks but I'll see if I can get an educational license from somewhere.

I'm curious how well the actuators work without the extra tension from the bands; is there a "dead zone" in the middle of the stage's travel where the actuator swaps from "pushing" to "pulling", or are you able to get everything tight enough that it's not a problem?  I will look at your actuator column design with lots of interest!

Also, is there a reason you were keen to use the 40mm version of the stage - the 65mm version has longer travel and less mechanical reduction, so might be nicer to use with the slightly lower-magnification optics of the 6-LED webcam.

I have had also some issues with the optics not being perfectly vertical as well, and tracked it back to the objective clip being knocked over during printing.  The tell-tale sign was that the dovetail clip has a kink in it at the same layer where the higher set of struts attach it to the microscope frame.  I added some thin links to tie it down during printing, which helped a lot - but these may have been lost at some point.

I found the LS65 version of the microscope was big enough to fit my 6-LED webcam, though it may have been smaller than yours...

rwb27, 2018-01-26:
By the way, Nichia NSPL500DS are a nice colour of white :)  The bigger problem is controlling the white balance of the camera, which I've now got a handle on with the Raspberry Pi webcam, but might be tougher with the $3 ones, as the software drivers aren't so good...

Maaphoo, 2018-01-26:
Just set it up so that all of the files can now be be accessed at our [Grabcad Partner Space](https://workbench.grabcad.com/workbench/projects/gcdNX91ERp7bqt9L4qShbWUocFUTs5mGSUJrBRDMv18t7C#/space/gc52J7YD2yzbkF6CiBX4JVg2GCteN-_qHQ4ZVq_soT-AeQ).

Each of the main bodies is in its own folder (same design just different equations). Some of the other stuff we are using is on the partner space as well. Mainly, the box.

As for the actuators, there is a slight bit of lash when reversing direction. Maybe 15 degrees of revolution? Not too much. I tried scanning past the change from push to pull a number of times and didn't notice a dead spot. If it is there, it seems small. My guess is that if it is an issue, it would be an issue for the motorized version during automated operation. It would be much easier to evaluate the performance of this setup with a motorized microscope.

As for the stage height, I did it justto reduce the number of layers and print time. In retrospect, the ability to use the normal objective clip would be much better as the small version that I'm using doesn't have much flex and requires post processing to get everything to fit together. I'll play around with the LS65 and see if I can come up with a better solution that what I have now.

Thanks for the tip on the LEDs and the objective clip angle.

Maaphoo, 2018-01-26:
Oops forgot to mention that if you just want to view Solidworks files you can do that in Grabcad. You can also use [eDrawings](https://www.solidworks.com/sw/support/edrawings/e2_register.htm).

rwb27, 2018-01-30:
Thanks for that - it looks really nice.  15 degrees is a fair bit of backlash, so might not be an option for the motorised version, but if it makes the assembly less painful and avoids needing a bunch of parts, it might be a good trade-off for the manual ones.  I've not measured; would your optics adapter fit the LS65 stage, or would it need to be wider than that?  I think your clip is 20mm from the centre, so I'm guessing not!

Also, how do you fit the lens into the model - does it just push-fit, or do you screw it in from underneath?

Maaphoo, 2018-01-30:
Did some testing today. Looks like I had the lash issue pretty much backwards. With my home brew testing setup, I wasn't able to measure much any lash when changing directions if the axis was away from the neutral point. At the neutral point, I did record much more irregular movement.  I wonder if in addition to the switching from push to pull, strings and actuator support stubs left over from printing are hanging up on the actuator a bit. Maybe my setup was just too crude.

I hot glued a protractor to one of the axes and made a stop with a pen. Pretty home brew, but it seemed to work ok. I took a picture every 5 degrees of rotation and then measured the distance from the edge of the image to a notable item in the field of view. Here's the setup and the results:
[image]

[image]

The problem that I had with using the LS65 stage is that the webcam would have to be inserted into the microscope above the objective clip before the mounting bracket was put in place. Then the webcam would have to be attached to the bracket while "in the cage" which seemed a bit tricky. Did you have another method of assembly? Here's an image of how the LS65 looks with the 6 LED optics package in place. Definitely some interference in there:
[image]
One thought I had was to make the entire stage removable except for a frame that attaches to the legs. Then the optics could be inserted from above and the original and much better objective clip could be used.

Finally here is how the optics all fit together. Yes the objective is just press fit into place:
[image]

rwb27, 2018-05-18:
STICLab have put together an OpenSCAD version here: https://github.com/sticGit/cheap_webcam

rwb27, 2018-05-18:
Also, @Maaphoo if it's useful to you, I do have a version of the optics module that has a slightly flexible push-fit for the M12 camera lenses.  If you're having quality control issues with them not fitting, this might be of some help: https://github.com/rwb27/openflexure_microscope/blob/master/builds/optics_m12_m12_lens_LS65.stl (from optics.scad with the camera and lens set accordingly).

rwb27, 2018-05-23:
hey, that looks really nice.  I'd love to see one - any chance there might be a microscope (or even better, yourself) in Nairobi in mid-June?  I've sent an email about dates.

In terms of the push-fit, I don't have photos but I'll pop to the lab now and see if I've got the bits to take one!

rwb27, 2018-05-23:
[image]
[image]
[image]
[image]
This is for a different Chinese USB camera with M12 lens, but I'm hoping they are sufficiently similar.  NB the distance from lens to sensor is waaay too long for the $3 webcams.

Maaphoo, 2018-05-23:
Thanks for the clarification. I was having trouble seeing how it fit with the microscope I think because I was confused about the length.

Unfortunately I won't be in Nairobi, but Solomon should have a number of the new design printed by the time you arrive. We are planning on making 10 next week.

rwb27, 2019-01-21:
Some possibly-useful updates:
* I've released a new version of the microscope which fixes a bunch of problems.  It also includes a "platform" mount for the Pi camera, which is not dissimilar to your mount for the USB webcam.  We should probably adapt a version of it to mount the 6 LED camera.
* STICLab have made a version of this, there is an (old) copy of their files in [their Github repo](https://github.com/sticGit/cheap_webcam/), and a newer version on google drive somewhere (ask and I'll post it if you're interested), though that's build against a previous iteration of my stage and won't work with the current master branch...

rwb27, 2019-02-27:
As of now, the latest release can be built using a camera platform that fits the 6-LED webcam.  Currently it's just a bit of tape that holds the lens onto the webcam, I think this can be replaced in due course with a nicer adapter (e.g. STICLab's one, or Matt's one).  However, as there is now support for this on the master branch, I'm going to close this issue :)

rwb27, 2019-02-27:
The part was added in a7df420e83af84bd858f0e12f3acc1ce278ed2b3, it's possibly missing from the builds directory but will build with the build script - so it will make it into the next bugfix release.

closed 2019-02-27 by rwb27

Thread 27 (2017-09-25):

### ISSUE TITLE
Ability to change heigh of objective

### ISSUE THREAD

**Issue by dborgesr** [rwb27/openflexure_microscope#27]
Hey, firstly i wanted to say incredible project! i've already printed and built 3 microscopes. 
I've already tried to get the RMS objective version working but ran into the issue that the objectives themselves are not all a standard height.

I know this request is way far out (i'm currently learning Fusion 360 to help out with the implementation), but I was wondering, would there be a way to make the height of the lens assembly tunable? Maybe have some sort of rung system built into the slide that's already present or something of the sort, this would allow immediate use of any objectives, even cheap ones you can buy off amazon, making this microscope ready for prime time.

--Cheers

**Comment by rwb27** [comment]
Hey,
  always great to hear from someone who's built it!  I've found two common objective sizes, which are 25mm and 35mm (this is the "parfocal distance", measured from "shoulder" at the top of the thread on the objective to the sample (which may or may not be more or less the same place as the top of the objective).  The LS65 stage and the optics modules in the STL folder are set up for 25mm objectives.  To work with 35mm objectives, I usually use the same set-up, but add a [10mm thick spacer](https://github.com/rwb27/openflexure_microscope/blob/master/stl/sample_riser_2_base.stl) on top of the stage to raise the sample.  The one I linked to has a handy sprung [clip](https://github.com/rwb27/openflexure_microscope/blob/master/stl/sample_riser_2_clip.stl) to keep the sample in place.  Alternatively you can use an LS75 stage, which is 10mm higher.  NB you also need the [LS75 illumination](https://github.com/rwb27/openflexure_microscope/blob/master/builds/illumination_and_back_foot_condenser_LS75.stl), which is taller.

  For more fine-tuning, it's relatively easy to adjust the spacing of things in the [optics module source](https://github.com/rwb27/openflexure_microscope/blob/master/openscad/optics.scad), the ``objective_parfocal_distance`` argument allows you to set the distance from the top of the mount to the sample.  This relies on having microscope_parameters set up correctly to match the microscope you're trying to build.

Any of that make sense?  I've not found a nice way to get serious adjustment of things like parfocal distance with one plastic part, instead I'm embracing the joys of parametric CAD and doing the adjustment before it's printed - but if you can come up with a solution, that's great.

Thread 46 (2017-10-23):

rwb27/openflexure_microscope #46: 3D Printing - too much supportive material required

wcolemanred, 2017-10-23:
Two different 3D printing companies have reported that tube_lens_tool, optics_picam2_rms and body_ss have thin walls while optics_picam2 and body_ss  and have overhands, all which will require lots of support structure. 

One 3D printer has suggested that 45 degree supports on any overhands are added to enable printing without support structures.

Is that possible?

rwb27, 2017-10-23:
Hmm - it would be fine to make a thicker version of the tube lens tool if that is a problem (it's just a cylinder slightly smaller than the lens, to allow you to push it into the holder).  Looking at ``openscad/tube_lens_tool.scad``, the wall is 1mm thick which ought to be OK for most printers - did they give you a figure for the minimum wall thickness?

I print both of the parts you mention that have overhangs on my printers (an Ultimaker 2+ and a RepRapPro Ormerod) with no support material, and no problems.  They have been designed very carefully to print OK despite the bridges (there aren't any "overhangs", only "bridges" - this is an important distinction, because bridges (i.e. where you are printing between two walls) are generally possible whereas overhangs (e.g. printing a diving board) generally aren't.

The microscope design has been through a lot of iterations to get it to print nicely without support.  If you just analyse it with an automated tool, it will usually tell you that support is required.  However, it's not, at least not using a RepRap-type plastic extrusion 3D printer.

Do let me know how you get on - I've never actually had them printed by an external service, so it would be interesting to know how it turns out and (if they don't mind you sharing it) how much it costs.

rwb27, 2017-11-13:
Hello, I was just wondering if you'd gotten any further with this one?  It would be good to know if you managed to get one printed in the end...

rwb27, 2017-11-21:
I'm closing the issue as I've not heard back - but do re-open it if you have anything further to add.

closed 2017-11-21 by rwb27

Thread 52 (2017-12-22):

rwb27/openflexure_microscope #52: Illumination Arm Question

SuAdams, 2017-12-22:
Working on the WEF project, and have concerns about whether we have the correct illumination arm for the body.

Both were the SS models, but the illumination arm is far higher than depicted in any of the photographs which you have.  I wanted to check that the SS arm and SS body which we had printed from the 5.16 zip file and are correct. 

Also, I'm not sure whether the focus is on the sample itself; I'm concerned that it is on sample slide/glass instead.  Do you have any advice on this?

FYI, I have built 2 versions of the microscope which we've had independantly printed.  Of the two versions, one version is complete, the other, just the main body and actuators.  This is because one is low quality and the other high quality.  You may be interested to know that whilst the low quaity version works (with just 2 parts needing the high quality) the high quality print is far easier to assemble.

We also found it very difficult to get hold of hex head screws which were also hex socket.  I went for a 30mm hex socket cap head solution with an additional nut at the top of the screw to resolve.

I've made notes of the build and would be happy to share.

rwb27, 2017-12-22:
I think that might be my fault - sorry!  As there are now over 100 possible configurations of the microscope, it gets increasingly hard to make sure the right bits are compiled with the right filenames, so I've switched to an automatic build system.  I've not yet built that into "release" archives, but if you head to the [builds folder](https://github.com/rwb27/openflexure_microscope/tree/master/builds) and grab the SS version of the illumination from there, it should be correct.

I do need to update the release version, but I keep putting it off because I think I'll have the build server running soon!

If you're using a Raspberry Pi camera module v2, I've found that you can't focus all the way through a standard-thickness microscope slide.  That means you usually need to either put the sample on the bottom of the slide (which is easier if you use a coverglass) or use a thinner slide/large coverslip.  The first version of the camera module had lower resolution, but a longer working distance, so you could focus through a slide (which was very useful).

I'd be curious to know what print settings/nozzle size correspond to "low" and "high" quality, and which bits you needed to print high quality.

Getting hold of hex head screws that small is annoying, I know - but your  solution (which I'm hoping you saw in the documentation) works just as well.  I buy mine from Anglian Fasteners, but you need to order quite a few to make it worth the postage!  I tend to buy a few hundred at a time...

Please do send me your notes - or even better upload them as a [build report issue](https://github.com/rwb27/openflexure_microscope/issues/new?labels=build%20report).

rwb27, 2018-01-09:
I don't think there's anything outstanding here, so I'll mark this one as "closed" for now.

closed 2018-01-09 by rwb27

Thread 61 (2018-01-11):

rwb27/openflexure_microscope #61: Robo R1 plus - printing issue

TanOneDeg, 2018-01-11:
I've had this printer for about 1 1/2 years now with no printing issues and have printed quite a few things of my own design.  Since I've had no problems with the printer, there never was a need to manipulate any of the settings other than the heat. For starters I don't know how any 3D printer of 'this type' would be able to print the horizontal members between the columns on the test print since it can't extrude anything onto air. Even so I gave it a try and as I expected it didn't print.  I'm still using the slicer that shipped with the Robo R1 plus which is MatterControl. I realize better slicers exist. My Robo has printed everything I've designed, including molds, gears etc., with no issues. Then again everything I've designed didn't require supports of any type. 

So I printed the test .STL and have attached an image of it. I didn't scale it, just printed it. Even if I would have printed a half dozen of these at once to give each one more time to cool, I still don't see how the horizontal members would ever print without some sort of support under them.  

Since one of my hobbies is micro/macro photography (mostly imaging diatoms with a microscope) I thought the openflexure microscope project would be interesting to try (as time allows).

 https://www.matterhackers.com/store/l/mattercontrol/sk/MKZGTDW6

Regards ...

[image]

rwb27, 2018-01-11:
I think we have different ideas of "didn't print" so thanks for the photo!  While the printed part isn't a perfect representation of the STL file, I would say that your test piece **did** print OK.  When bridging over an air gap, there will always be a little sag/spaghetti underneath (though it can be reduced if you keep the temperature relatively low, don't print too fast, and use a slicer that handles bridges well).  The top bridge (which is the only one that matters) looks perfectly solid, although I've seen neater.

The microscope has been designed to tolerate printing artefacts, like rough surface quality and gunk under bridges - so I would be hopeful that it will still work nicely if you print it on your machine with whatever settings you used for the test piece.  If you wanted to try for higher quality, I'd suggest giving it a go with slightly lower temperature - that helps the plastic to stretch over the bridge without sagging or forming loops.

The two thin bridges are only there to stop the legs being knocked over during printing and don't serve any purpose afterwards, so if they look ugly you can snap them out with pliers quite easily.  The bridge at the top is important, but while it's not the neatest bridging I've seen, it has also spanned the gap pretty well.

[image]
I've attached a photo of a part I had on my desk to show what the part looks like on my Ultimaker 2+.  You can see there is still a little sagging and a few loops of plastic under the main stage, but the bridges have printed without too much junk underneath them.

TanOneDeg, 2018-01-14:
The top bridge (not the block on top of it) didn't print very well in my opinion. May I ask why the top bridge, or even the others for that matter, are horizontal instead of arched (gusseted support)? Seem like the top bridge would print perfectly and even be stronger/stiffer if done so.  Naturally I will give it another shot. I did drop the temperature down to 191c on my first attempt (using PLA).

rwb27, 2018-01-16:
I think it wasn't brilliant, but it was still good enough to work :)

There is a very good reason to keep the bridge horizontal, which is that it's intentionally not rigid; the motion of the stage comes from bending the thin bits of plastic at either end of the horizontal part (you should be able to distort the test leg print into a parallelogram).  Using an arch shaped bridge would make it impossible to have those very thin spans either side of the thick central strut.  If you can distort the structure so the angles are about 6 degrees away from right angles, without the thin bits breaking, that's the most important test.

Also, bear in mind that arched supports won't print nicely after about 45 degrees, so it's often preferable to continue up at 45 degrees then bridge across the top, even when the flexure hinges aren't needed.

If you're already printing at 191C I retract my comment that you might want to print cooler!  It's possible you'll find the whole thing just works better if you print the microscope body rather than the test object - the trouble with small, quick prints is that the time per layer is very short, so the object doesn't have time to set fully before printing the next layer.  I've often seen small parts print quite poorly, then printed multiple copies of the same thing and had it come out much, much better.

TanOneDeg, 2018-01-19:
Touching base with you Richard, 

Just to let you know, I went to the Robo R1 plus forum for suggestions on printing this.  A couple there that have extensive printing experience are going to give it a shot. None of them use the slicer that I do with the majority are using Simplify3D.  As I posted there, I'm not trying to beat a dead horse to death. I printed the **main_body_LS65.stl** last night, acquired from the Github site, with no supports, temp set at 189c using MatterControl and this is how it turned out.  Obviously it isn't cleaned up.  This is how it looks right off the print bed. I didn't take the time to use the proper diffusion to eliminate the specular highlights in the photographs below. 

[image]
[image]
[image]
[image]

 Of course I'm not happy with the results but I am surprised the entire model printed.

rwb27, 2018-01-20:
Thanks for posting the pictures - that's really helpful.  It looks like a perfectly good print to me, obviously the thin stringy bits aren't beautiful, but they should be easy enough to clean out and won't affect the function of the microscope stage.  Normally when I've had stringy bits like that it's because I'm printing too hot (but at 189C I'd be surprised if that's the case for you) or not using enough retraction.  However they are usually just a cosmetic defect.  I'd consider your print a solid success :)  Do post if you build it into a working microscope, and if you have a link to the R1 forum when anyone posts their results I'd also be keen to see it :)

All the best,

Richard

TanOneDeg, 2018-01-20:
I will let you know the results of others that may print this.  I wasn't happy with the model at all. The stringy stuff will be super easy to remove and doesn't have an effect on the final print. There are other areas that are unacceptable (to me)  and difficult to photograph.  With respect to your design, I still think designing gussets (probably around 30 degrees or so) at key places would be helpful in printing, especially on the top horizontal members on the towers and maybe incorporated in the supports for the physical stage platform.  Is the 3D model available for editing and downloading?  I will still experiment with my printer, I haven't given up. 

https://www.matterhackers.com/news/how-to-use-support-material-part-1

rwb27, 2018-01-22:
One of your comments seems to have vanished - that's odd!  The CAD files are all in this repository, in the OpenSCAD folder.  They are made in OpenSCAD, a free script-based CAD program.  You will need to download all the files and put them in the same folder, as the main body depends on several other files.  If you can find ways to make the print neater/more reliable by adding supports (whether they can flex with the structure or need to be snapped off after printing) I would be very interested.  It prints pretty well now but there is always room to do better.

The missing post also contained a link to a really helpful page on what printers can and can't do, including a discussion of bridging and support in various links:
https://www.matterhackers.com/news/how-to-use-support-material-part-1

TanOneDeg, 2018-03-06:
Richard,
Do you have pictures and/or a video of a working Openflexure? Just wondering. 
Regards,
-JW:

TanOneDeg, 2018-03-12:
Could this be printed with a SLA printer and work as designed?

rwb27, 2018-03-12:
I can't see any reason why not - though I don't have one to test with.  I guess you'd need to make sure the resin is sufficiently flexible, but I would guess that even the relatively rigid resins should be OK.  If you have access to an SLA printer and try it out, let me know :)

TanOneDeg, 2018-03-12:
... I was thinking Standard Nylon (SLS) PA 12 with 50um layer height?

TanOneDeg, 2018-03-12:
Never mind ... looks like they can't print it without supports and said they would be hard to remove.

rwb27, 2018-03-13:
Hmm, that's a shame.  It was put together very much with fused filament in mind, so that's not a huge surprise.  That said, the supports usually used for SLA are much easier to use than the ones for fused filament, so they might not be such a problem.  I've been told in the past that the large flat base of the body (which is necessary for adhesion on a filament deposition printer) could be a problem with SLA; I'm not sure if there's an easy way round that - though possibly printing it in a different orientation might help.

TanOneDeg, 2018-03-18:
Richard,

I cleaned up the flexure stage today but I haven't a clue if everything printed correctly. I did remove all of those braces since they didn't print to begin with.  Everything seems to flex properly when I press the flexure tabs on the bottom of the stage.  After looking at the image below and if you agree that it appears to be printed correctly what specific items would you suggest I print next? Also is there anything I should check for printing failures on the stage below?

[image]

Thanks again,
-JW:

rwb27, 2018-03-19:
Hello - that looks like an absolutely beautiful part to me!  I put together a little list of [quality checks](https://github.com/rwb27/openflexure_microscope/blob/master/docs/images/microscope_body_quality_checks.pdf) for some folk working on establishing a baseline of prints to measure reliability, etc. (I really ought to put this somewhere more obvious), I think yours will pass all the checks with flying colours.

Next, you'll need feet, gears, an illumination arm, and an optics module.  The exact files you need will depend on what camera and lens you are planning to use - I have tried to detail all this in the readme in the [builds folder](https://github.com/rwb27/openflexure_microscope/tree/master/builds/) but feel free to ask if you're stuck.  One of these days I will get round to making a form that simplifies the process of choosing the parts...

closed 2018-12-05 by rwb27

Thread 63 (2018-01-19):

### ISSUE TITLE
M3 Thumbwheel Screws - 6 Nut Issue & Solution

### ISSUE THREAD

**Issue by SuAdams** [rwb27/openflexure_microscope#63]
Last week 2 adults, who will be mentoring youth at the event, built the microscope. Subsequently 2 14 year olds tested the build at the weekend.  

Both times the pairs experienced the same problem; when trying to focus the image, the centre thumbwheel unwound.  

I have adjusted the instructions for our version (which uses 6 nuts in the actuator build) to use 2 x 25mm M3 screws on the outer thumbwheels, and 1 x 30mm M3 screw for the centre thumbwheel.  This appears to resolve the problem nicely.

**Comment by rwb27** [comment]
Thanks for that - I've included that in the documentation in 2688ac6.  If you felt like updating the [wiki page](https://github.com/rwb27/openflexure_microscope/wiki/Non-printed-parts) that would also be brilliant :)

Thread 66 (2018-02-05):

### ISSUE TITLE
baseplate mount holes fused with stage on SS40, v5.17.1-5540

### ISSUE THREAD

**Issue by Sammy93** [rwb27/openflexure_microscope#66]
![image](https://user-images.githubusercontent.com/3144547/35739503-b0fad248-0829-11e8-9e39-c34f171194a5.png)

As a result, the stage is stiffer and X/Y travel is decreased.

**Comment by rwb27** [comment]
Thanks for the nice clear photo.  I don't know when this happened, but I have now fixed it in 9fe004d427fbe358df5adee427e7eb3ab92424ce.  Sorry for the wasted print...

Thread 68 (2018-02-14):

rwb27/openflexure_microscope #68: Question about high resolution optics module setup

zachjacobs, 2018-02-14:
Hello,

Great work here!  I'm still a bit confused about how the optics will work with a given objective lens.  I have found [objective lenses](https://www.amazon.com/dp/B01G5W0UH4/ref=psdc_3117833011_t1_B00FG8BC62) that are RMS compatible, and designed for 160mm tube-length finite-conjugate microscopes.  I am planning on pairing these with this [50mm tube lens](https://www.thorlabs.com/thorproduct.cfm?partnumber=AC127-050-A) from thorlabs.  This leads me to believe that I should be using the optics_picamera_2_rms_f50d13_LS65.stl file to put this assembly on a raspberry pi 2 camera.  Is that correct?

When using a finite-conjugate objective lens, I have read that you typically you want a 160mm tube-length.  Does the 50mm tube lens redirect the focus to make the finite-conjugate lens compatible with a 50mm tube?

Thanks again!

rwb27, 2018-02-15:
Thanks.  You might be confused, but you are also 100% correct!  The optics module you mention is correct for an RMS objective, the ThorLabs tube lens, and a Raspberry Pi camera module v2.  Looking at the Amazon link you included, I think you have 35mm parfocal distance lenses, so you'll need the LS65 (or LS65-M) body, and you won't need a riser on top of that, so you should also use the LS65 illumination module.

Any suggestions on how I could have explained that more clearly are appreciated - I think GitHub might even let you send me a pull request to update the readme file through the web interface.

Have fun, and do let me know how you get on - it is always lovely to hear people's build reports and what they use the microscope for!

rwb27, 2018-03-19:
Closing this because I think I answered the question - and you did manage to figure it out correctly from the instructions in the first place :)

closed 2018-03-19 by rwb27

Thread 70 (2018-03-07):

rwb27/openflexure_microscope #70: main_body_LS65-M.stl

sh969, 2018-03-07:
New optics module mount:
It is a very complicated procedure to losen the screw each time I need to do modifications to the optics module (e.g. changing objective) since the centre gear (+motor) has to be unmounted as well. I much prefereed the old the clip-on solution.
The bended design of the centre actuator makes it very hard to attach its rubber band in the first place (even with new, longer tool).

Endstop screwholes:
The optical endstops are colliding with the z-actuator. It would help to move the screws a milimeter towards the outside (away from the centre).

rwb27, 2018-03-12:
Hello, I agree the new screw position isn't great.  There might be scope for a more complicated mechanism that puts the screw in a more accessible location, but I was waiting to check that the new z axis worked first.  The old clip-on solution works fine for a month or two, then the plastic loses its elasticity and the objective falls out the bottom of the microscope!  That's a bit of a problem, hence the change.  Using the new arrangement also results in a smaller, stiffer assembly.  I just need to fix the screw position and it will be lovely!

I should make a revised foot to fix the issue with band insertion, that oughtn't be too hard.

I can also shift the screw holes

sh969, 2018-04-06:
Successfully assembled the new version and I am quite happy with the stability of the optics module.

Two small issues:
1) The screwholes for the end-stops are still not quite fitting. I'ld suggest we move them ~4mm away from the optics module (towards the outside) and another ~3mm overhanging (there are pins under the endstop to connect them to the Arduino, so the sensor can only be mounted tilted as of now, see image 1). 
2) For some reason our 3d printers here in Maxwell (Ultimaker 2) are printing the optics module with a opening too small so the Raspberry Pi camera does not fit (even though the stl file looks fine). See red and yellow objective mount on image 2. The black one was printed somewhere else and looks how it is supposed to. Might be due to the fact that the cutout is on the bottom. I had to carve it out to make it fit. It was not easy at all to get rid of the extra material. Maybe just extend the opening depth in the design file.

[image]
[image]

rwb27, 2018-04-26:
We discussed the wierd opening and didn't get a solution - it seems quite hard to reproduce!

The issue with the difficult screw is (more or less) fixed in abb831b, which moves the access hole to the side, rather than above, the Z adjuster gear.

herbzhao, 2018-07-02:
The screw for the objective module takes some practice to install, but it works fine. However, is it possible to keep both push fit and screw? 

Holding the screw and optics module in place at the same time is difficult. Also, when loosening the screw to move the objective module, it may just slip down immediately.

rwb27, 2018-07-03:
It's hard to keep the push fit and the screw, in part because I am keen to make sure it self-centres, which I think would be difficult if I combined the dovetail and the screw.  If you can think of a way to make the old dovetail clip work with a screw I'd be interested - but I think it might be easier to change the new version slightly rather than reverting to the old one.

Currently, you can put the screw in, then twist the nut onto the end of the screw (usually just one turn, so there's plenty slack), then slide the optics module up onto the nut.  I think it might be easier if the nut is permanently mounted into the objective, and the screw can then be put on the objective, and inserted into the microscope through a slot.  I might have a go at doing that when I get a moment (!)

rwb27, 2018-07-25:
I think this is covered by other issues now - I'll close this one.

closed 2018-07-25 by rwb27

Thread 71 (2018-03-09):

rwb27/openflexure_microscope #71: hybrid lens adapter for v1 AND v2 cams?

jywarren, 2018-03-09:
Hi! At Public Lab we're using the lens adapter part as part of a simpler "basic" microscope kit (a stepping stone to this project to help onboard newcomers) -- https://publiclab.org/notes/partsandcrafts/02-15-2018/2-attaching-your-raspberry-pi-camera-to-a-microscope-objective-lens

We notice that first-timers often mix up v1 and v2 cameras, and were wondering if anyone could post an stl for a lens adapter that would just fit either one -- that way we can skip a step and just smooth out the build process. Any help appreciated!

rwb27, 2018-03-10:
Hi - that's cool, I didn't realise you were using it for that.  Have you tried the latest version of the v2 optics (from the builds folder, [optics_picamera_2_pilens_SS40.stl](https://github.com/rwb27/openflexure_microscope/blob/master/builds/optics_picamera_2_pilens_SS40.stl))?  Because I've changed from push-fit to screw in (to help stop people destroying the flex cable) I *think* that should fit either, but it may be that the cut-out on the camera module is not quite right.  I don't have many v1 modules any more to test with, so if you could check that would help.  If it doesn't fit, it should be possible to tweak it fairly easily, so let me know and I'll see if I can come up with a universal version.  I think the lenses are similar enough in size that they should both fit the new mount, which is slightly flexible at the top.

jywarren, 2018-03-12:
Oh wow, thanks!!! 

Yes, i think there are some clearance issues, specifically in the two boxes I've drawn here:

[image]

The onboard camera ribbon attachment goes much closer to the edge of the adapter, so it needs half or more the width along that edge (at the top of this image).

There's also some tiny components (in the left-hand box region) that don't clear and I had to hollow out just a tiny bit of space for them. I'll post a picture of the board itself too.

jywarren, 2018-03-12:
Ah, here's a really good one, actually: 

[image]

steviepubliclab, 2018-04-12:
Hi! Also looking for modifications to the bottom piece to fit the Rev 1.3. This would be cutting out a window on the side opposite the screw holes. If you're holding it with the open side facing up, the widow needs to be towards the left hand side. 

See below:
[image]

[image]

[image]

rwb27, 2018-04-17:
Hi, I've taken a stab at this in the [unified picamera mount branch](https://github.com/rwb27/openflexure_microscope/tree/unified_picamera_mount/), specifically I've put up STLs in the builds folder for the three versions of the picamera optics module - e.g. the [SS40 version](https://github.com/rwb27/openflexure_microscope/blob/unified_picamera_mount/builds/optics_picamera_2_pilens_SS40.stl) that uses the pi lens.

[image]

I've yet to test this out - if anyone interested fancies printing one and checking, that would be super.

rwb27, 2018-04-17:
I'm going to leave it called "picamera_2" for now, because the lens removal tools are still specific to that version.  I can probably find an STL for the board gripper that works with v1, but I never did manage to make my lens removal tool work with v1, it's v2 only.  I'm also surprised there are still people building with v1 modules - I thought they were discontinued?

jywarren, 2018-04-18:
We're ordering lots of v1.3 modules via Alibaba and Aliexpress -- pretty good, and much cheaper! 

Thanks so much for this adaptation, @rwb27 -- we're definitely going to test it out and will get back to you. 

Much appreciated! 👍 🙌 🎉

rwb27, 2018-04-19:
no problem.  If you're able to measure where the window needs to be in the back part, it should be easy enough to add a modification in - even better, you might be able to do it directly in OpenSCAD and send me a pull request - https://github.com/rwb27/openflexure_microscope/blob/master/openscad/cameras/picamera_2_cover.scad will generate the cover as you have it now, so you'd just need to take the difference of the current cover and a rectangle that chops out the relevant bit, and call it picamera_1_cover.scad.

rwb27, 2018-07-05:
@jywarren did this work for you in the end?

rwb27, 2018-08-09:
I've pulled this into both the master branch and my current development branch - I will close the issue for now but please do re-open it if you figure out how to modify the cover, and do post back to say if the hybrid part works for you :)

jywarren, 2018-08-09:
Hi, @rwb27 -- sorry, ok, we'll test this one -- https://github.com/rwb27/openflexure_microscope/blob/master/builds/optics_picamera_2_pilens_SS40.stl

If that works, have those geometries been adapted into the RMS designs as well? Thanks and sorry it took us a while to test this out!

jywarren, 2018-08-09:
This commit seems to indicate so! https://github.com/rwb27/openflexure_microscope/commit/7eefc52800669a2fc5e880acf5dff288f766a058#diff-d862a606811deb350fed830c41b0f0f2

jywarren, 2018-08-09:
Looking at https://github.com/rwb27/openflexure_microscope/blob/4eecaadd426169f551a0be46a430c6b15da4e1c7/builds/optics_picamera_2_rms_f50d13_LS65.stl and https://github.com/rwb27/openflexure_microscope/blob/4eecaadd426169f551a0be46a430c6b15da4e1c7/builds/optics_picamera_2_rms_f40d16_LS65.stl

rwb27, 2018-08-10:
hmm, looking at the STLs I think that might not be the case - only the SS40 one looks right.  If you could check that one actually fits, it oughtn't be a big deal to recompile the others.

jywarren, 2018-08-30:
Hmm, actually all three fit! 

https://github.com/rwb27/openflexure_microscope/blob/master/builds/optics_picamera_2_pilens_SS40.stl

and:

https://github.com/rwb27/openflexure_microscope/blob/4eecaadd426169f551a0be46a430c6b15da4e1c7/builds/optics_picamera_2_rms_f50d13_LS65.stl

https://github.com/rwb27/openflexure_microscope/blob/4eecaadd426169f551a0be46a430c6b15da4e1c7/builds/optics_picamera_2_rms_f40d16_LS65.stl

They all three seem to have the same cutouts in the base:

[image]
[image]

rwb27, 2018-08-30:
Yes, I think I recompiled them all after I realised that. They are definitely all the new universal cutout :)

jywarren, 2018-08-30:
fantastic, and thanks so much!

rwb27, 2019-01-14:
By the way, if you are not using the dovetail on the side to mount them, you might want to check out the new "lens spacer tube" that I'm using in the upcoming release - this is the part you see above but without the mounting.  It's designed to screw on top of the camera, mounting to four M2 holes in a baseplate.  I'll close this issue for now, but do shout if there's anything further I can do to be helpful :)

closed 2019-01-14 by rwb27

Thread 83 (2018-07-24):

rwb27/openflexure_microscope #83: Importance of the elastic bands for the motorized setup

fanneaup, 2018-07-24:
I reproduced the openflexure (SS40 with motors) microscope and adapted it to work in reflection.

However, I am having trouble getting smooth, repeatable motion from the motors. I was wondering how important the type and size of elastic bands was or if anyone had come across the same issue.

rwb27, 2018-07-24:
The elastic bands are generally pretty important - assuming you're using the latest version, you should be using the 30mm inner diameter, 2mm thickness Viton O rings.  These can be ordered from e.g. simplybearings.co.uk.  Using a band that's too strong will cause the stage to stick while it moves, while a weak one will mean that for a large part of its travel, the microscope flops around erratically.

Your choice of screw/nut can also have an effect; brass nuts on stainless steel screws with a little grease is my preferred option.  What are you using for the motors?

If you upload a picture or two here (you should be able to drag and drop them) I'll have a look - sometimes there's something obvious in the picture.

fanneaup, 2018-07-25:
[image]
[image]

Thank you for your answer.

Pictures of my setup are attached. The motors are 28BYJ-48 with their ULM 2003 driver boards. they are controlled by the GPIO pins of the Raspberry Pi 3 B that I am also using for the microscope but they are alimented by an external power supply.

When it comes to the screws and nuts, both are made of steel and I have put some WD40 as lubricant.

Eventually, the elastic bands seem to be 2x1mm width and 50mm of diameter but I have cut them to make them thiner and tighter.

rwb27, 2018-07-25:
ok, looks like you've assembled it nicely, and you have the current master branch version - excellent.  The rubber bands will most probably be less strong than the Viton O rings, given that you're only in Bristol I can probably get some O rings to you relatively easily.  The best way to test if the bands are doing their job is to unscrew the large gear until there is a visible space between the gear and the column it sits on.  You should then look at the bottom of the microscope, and check that the actuator has been pulled down - I think the tip of the actuator should move about 4mm down, so the edge of the wider part moves by something like 2-3mm.  If it's not protruding down as much as that, the band is too loose/not strong enough.

I have never used the GPIO pins on the Raspberry Pi to control the motors, so I don't know how good the timing is; are you using half-stepping, and how fast are you stepping the motors?  I would usually trust an Arduino more than the Pi GPIO pins, because its timing is better.  If you can get hold of a Nano (or equivalently an Uno) you could use the [[rwb27/openflexure_nano_motor_controller]] firmware (and Python module).

fanneaup, 2018-07-25:
Ok, I just did what you said ("unscrew the large gear until there is a visible space between the gear and the column it sits on") and it looks like this: 

[image]

So the edge of the wider part moved down closer of 1mm than 3mm. I can make it move down to 3mm by tighening the elastic bands again but then the stepper motors seem to be blocked by the elastic and are not able to move.

In order to rotate the stepper motors, I am currently using half-stepping with a delay of 0.003s (value chosed according to the datasheet). But, at the beginning, I had tighter elastic bands that did a great job on the actuators but I thought they were to strong for the motors (as they were stuck and enable to rotate) so I tried normal stepping with the same delay as I had read it would give them more torque but it was unsuccessful. To fix that, I have loosened the elastic bands to allow my motors to rotate but maybe it came from the timing of the Pi as you said because it does not give me a smooth motion.

rwb27, 2018-07-25:
hmm, ok.  The picture you've pasted in up there looks about right - are you sure that's only 1mm?  I'd say the elastic bands are probably fine as you have them.

It may well be worth trying an arduino, if the Pi is skipping steps that would explain it.  I have also had issues with one (or more) of the pins driving the motor being disconnected - this often shows up as a drop in torque.

Lastly, I tend to go for grease rather than something like WD40; it lasts longer and results in smoother motion.  Brass nuts are also worth getting hold of - it feels noticeably smoother.

voxelman, 2018-11-09:
WD40 is not a particularly good lubricant for threads because it evaporates. It is actually a water displacement solution. It would be better to use a thread lubricant grease. For that I would say that Google and Amazon are your friend.

rwb27, 2018-11-12:
thanks - my current favourite is either sewing machine oil (very light, wicks well into the M3 threads) or 3-in-1 (also fairly light, and easier to find).  That said, I think what the grease was mostly doing is lubricating the washer on top (between the plastic gear and the top of the microscope.  I find that two washers + grease makes the biggest difference, and the next biggest improvement comes from using decent steel screws (I have some cheap screws that strip after a couple of days of heavy use).  Once you've got two washers and a decent screw, an appropriate grease/oil is definitely important, and I should add that to the instructions.

rwb27, 2018-11-12:
By the way @fanneaup could you post some details of how you're using it in reflection?  It's something a number of people are interested in, and I'd love to see how you've done it (and how well it worked).

rwb27, 2019-01-21:
This thread has gone quiet for a while - now that I have the new instructions out (which are clearer about the Viton O rings being the preferred option) I think it can probably be closed - but please do re-open it if there's more to add, or if you think the instructions could be improved!

closed 2019-01-21 by rwb27

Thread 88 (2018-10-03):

rwb27/openflexure_microscope #88: Mesh repair needed on main body

rwb27, 2018-10-03:
I've just started using Slic3r again, and noticed that there are some bad edges/faces in the STL of the main body in the cantilever branches.  I should track this down and fix it, as I think it causes printing issues on my Prusa, which is a shame!  It's probably a matter of looking back through old commits and finding the last STL that doesn't report any mesh errors, then looking at the SCAD files to figure out what changed.  Figuring out which STL is the last valid one shouldn't be too tricky, so would be a great way for someone to get involved without needing to learn OpenSCAD, and would save us a load of time...

voxelman, 2018-10-06:
I’ve printed the main body stepper motor version from the master in the past two weeks on my Original Prusa i3 MK2.5 without any complaints from the PE version of Slic3r. If the Slic3r fixed problems, I didn’t notice. I will check it tomorrow and let you know if I notice any irregularities. Thank you for the great work.

rwb27, 2018-12-17:
Hi @voxelman thanks for posting that - I think the version on master is OK, it was the version in the cantilevered_objective_mount branch that caused problems.  I'm now working on "reversed_cantilevered_objective_mount", and that seems to be OK again in Slic3r, though I am not sure what fixed it!  I am working on tidying up the branches so the development branch is more obvious...

rwb27, 2018-12-17:
as of f70bd71075a49a5887644b359ecbd21003f4c3e8 it seems to be valid, though reports as two shells rather than one.

rwb27, 2019-01-16:
I thought I'd tracked this down in OpenSCAD, because it was reporting that there were 2 volumes - but it seems that OpenSCAD always reports 2 volumes.  I came across a mailing list thread suggesting that CGAL consders the shape to be one volume, and the infinite space outside of the shape to be the second volume - so there are always two.

rwb27, 2019-01-16:
I've also had a closer look at the output from Slic3r; it looks fine in a G code viewer, but what my Mk3 is doing doesn't correspond to the contents of the G code file, I think maybe it has skipped some lines.  This is wierd, but I am starting to think it might be our printer and not the model.

rwb27, 2019-01-16:
Oh, and according to MakePrintable.com the LS65-M main body has "no issues" (although it does mention 29 non-manifold edges).

[image]

rwb27, 2019-01-18:
I have found the (current) problem - it was my printer!  The G code and STL were fine, I power cycled the Prusa and the body is printing fine now.  It's wierd that the errors were so consistent, maybe there's a particular combination of moves that causes it to skip stuff (like a curve with many short segments followed by a long line)?  Anyway, I think the STL is valid so I'm closing the issue :)

closed 2019-01-18 by rwb27

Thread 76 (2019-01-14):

### ISSUE TITLE
New illumination adjustment screws need nuts

### ISSUE THREAD

**Issue by julianstirling** [rwb27/openflexure_microscope#76]
After a few adjustments of the illumination the M3 bolt which just taps into the base becomes loose and cannot be tightened. Can nut slots be added into the STL for the base?

**Comment by rwb27** [comment]
Upgraded to the better triangular self-tapping holes, and added nut traps - they might not always get used, but the option is there, at least.  Currently there's no nut in the instructions, that's probably fine for now.

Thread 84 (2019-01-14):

### ISSUE TITLE
Objective hits hole in stage

### ISSUE THREAD

**Issue by rwb27** [rwb27/openflexure_microscope#84]
The high-res version has a 30mm hole in the middle, but the nicer objectives are nearly 25mm in diameter - which limits the travel.

As and when this gets fixed, I will also need to sort out the endstops.

**Comment by codeTom** [comment]
I have a version with larger hole, but I had to modify the rectangular hole underneath, its width is now hole diameter+2mm, UM3 printed these bridge fine with hole_r=19.5 see b9b09c8744aca0b5a74177f91af5fefd1c1fc4c1

**Comment by rwb27** [comment]
This will go into the release very soon - I think it's fixed, though we might need to update the sample riser as well.

**Comment by rwb27** [comment]
Sample riser is also fixed, marking this as done.

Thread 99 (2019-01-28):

### ISSUE TITLE
http://rwb27.github.io/openflexure_microscope/docs/parts/d13_f50_achromat gives 404 error

### ISSUE THREAD

**Issue by ctzurcanu** [rwb27/openflexure_microscope#99]
when clicked from page http://rwb27.github.io/openflexure_microscope/docs/2b_high_resolution_optics_module.html

**Comment by rwb27** [comment]
Hi @ctzurcanu thanks - currently the bill of materials (which includes the contents of the ``parts`` folder) is a bit of a work in progress - the intention is that it will be fully populated but I'm not quite there yet.   The part in question is an achromatic lens, with a focal length of 50mm and a diameter of 13mm (or more precisely, 12.7mm).  The easiest way to get hold of one is to order it from ThorLabs, as part number AC127-050-A.

If you are just checking out the project, it might be easier to start with the basic optics module - this is much cheaper and in particular doesn't need any specialist optics, just the Raspberry Pi camera module.

**Comment by rwb27** [comment]
I have done my best to keep the bill of materials reasonably complete in the first section of the instructions (perhaps confusingly named "printing").  I hope I've described things fully enough there, but I will try to add some more information on the specialist parts.

**Comment by ctzurcanu** [comment]
We really want to make something not only sensational but hopefully useful for Medicine. That is why we opted for maximum magnification that we could demo.

I found the part there for about 50 Eur. Will buy.

**Comment by rwb27** [comment]
cool - do let us know how the build goes!

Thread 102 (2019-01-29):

rwb27/openflexure_microscope #102: Build report

ctzurcanu, 2019-01-29:
First: I have discovered this project quite late for my purposes. I realized that I may need quite a long time to gather all the required pieces. (I have only one month to complete this and some parts require 2-3 months to arrive from China)

One example: 
https://www.aliexpress.com/item/High-power-LED-lens-diameter-13mm-Plano-Convex-lens-led-optical-lens-1W-3W-Reflector-Lens/1262190515.html?spm=2114.search0104.3.2.27c1304cILXAPH&ws_ab_test=searchweb0_0,searchweb201602_1_10320_10065_10068_10547_319_317_10696_453_10084_454_10083_433_10618_431_10304_10307_10820_10301_10821_537_536_10902_10843_10059_10884_10887_100031_321_322_10103,searchweb201603_59,ppcSwitch_0&algo_expid=dcb64a9e-830f-4a04-93d6-3106ed6a4c3a-0&algo_pvid=dcb64a9e-830f-4a04-93d6-3106ed6a4c3a

or:
https://www.aliexpress.com/item/4X-10X-40X-100X-Infinity-Plan-Achromatic-Objective-Lens-with-RMS-Mounting-Thread-DIN-45mm-f/32912050210.html?spm=2114.search0104.3.46.5df06a99vZWRd1&ws_ab_test=searchweb0_0,searchweb201602_1_10320_10065_10068_10547_319_317_10696_453_10084_454_10083_433_10618_431_10304_10307_10820_10301_10821_537_536_10902_10843_10059_10884_10887_100031_321_322_10103,searchweb201603_59,ppcSwitch_0&algo_expid=031a16ae-a830-45fa-8a77-18dad23fe003-7&algo_pvid=031a16ae-a830-45fa-8a77-18dad23fe003

But I will try to press ahead with the build.

I have ordered:
https://kitspace.org/boards/github.com/rwb27/openflexure_nano_motor_controller/
3x PCB
3x the rest of electronics minus the ICs, because the ICs will come with the motors:

https://www.amazon.de/gp/product/B0711TWN12/ref=ppx_yo_dt_b_asin_title_o00__o00_s00?ie=UTF8&psc=1

rwb27, 2019-01-29:
Thanks for starting a build report.

Regarding the optical bits, it's worth pointing out that the basic version works fine without the plastic lens (you can experiment with a piece of white tape or thin paper where the lens should go, sometimes that acts nicely as a diffuser).  That is one reason I tend to encourage people to build the basic version first.

Sourcing objectives and lenses from China is generally a bit slow, but suppliers in the UK (and I suspect many other places) are several times more expensive.  Objective lenses can be obtained from e.g. ThorLabs, Edmund Optics, Comar Optics, etc. but usually at a significantly higher price.  They tend to arrive next-day, though!

I've not found a good UK supplier of the condenser lens, more expensive glass ones are available from the companies above, but this is way more than we need for the OpenFlexure Microscope.

ctzurcanu, 2019-02-01:
Waiting for Godot...

I have most of what I need for 3 microscopes (all motorized)

[image]

Waiting for the 3 PCBs and the 3D printed parts.

ctzurcanu, 2019-02-06:
Half of Godot is here!
[image]

This is only a part of the printed parts :)
Used https://www.3dhubs.com/ for printing. The quality seems good.

ctzurcanu, 2019-02-06:
other small parts:
[image]

Now we can begin the assembly!

ctzurcanu, 2019-02-16:
Godot arrived! (the PCBs arrived, we soldered them)
Now having a setup problem: one time the install script worked well - now it does not more at #106 

[image]

ctzurcanu, 2019-02-16:
This software problem is the only one obstacle remaining. Now we are at home and able to find the last screws needed. 
The saddening part is that we made it to work couple of days ago. We played with the motors remotely. Now it seems to fail at the exact (past) success formulae.

ctzurcanu, 2019-02-16:
The microscope objective that I have here at home seems to fit the bill. 100x on oil. Looks like this:
[image]

ctzurcanu, 2019-02-19:
I have gathered all the needed bits. Here is one completed hi-res micro:

[image]

rwb27, 2019-02-20:
Well done, that looks like it's really nicely assembled!  The two base parts look identical though, normally the top one would be a different shape, to allow a bit more clearance for the optics module, and so that there are screw holes that match with the lugs on the micorscope.  Did you print the microscope_stand part, or two copies of the motor driver casing?

rwb27, 2019-02-20:
(it's worth pointing out that it should work either way, it's just that the version that screws together is a bit more robust).

ctzurcanu, 2019-02-20:
Ha ha ha! You caught me: I had to change and put the rasp-specific component first because this is the hi-res montage. Yes: optics needed more room to go down.

The parts need a bit of modification and would be truly interchangeable. with longer screws, one could screw directly into 2 of the feet.

ctzurcanu, 2019-02-20:
[image]
One first slide. this is lo-res

rwb27, 2019-02-20:
very nice :)

rwb27, 2019-04-30:
The repository is [moving to GitLab](https://gitlab.com/openflexure/openflexure-microscope/), and this issue has been migrated.  I'll close all the issues here in due course, but am leaving notices on all the currently-open ones.  If you head over to the other repository, this issue will be updated there.

closed 2019-04-30 by rwb27

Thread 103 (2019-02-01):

rwb27/openflexure_microscope #103: Sample clip mounting holes

jhitesma, 2019-02-01:
Working on building the 5.2 release.  Not sure choosing a beta release as my first try was a great decision but figured why not go with the latest and give some feedback - it's only a few hours of printing if I need to do it again.

So far it's going well and I haven't run into any real issues.  All the parts printed well and seem to fit well.  Finding suitable O-rings in the US has proven a bit difficult.  At least at the local level.  I found some at McMaster Carr but they won't be here until Monday and the only ones close I found find in town were too thick and either too big or too small so I may try and find some suitable rubber bands in the meantime so I can try it out this weekend.

There is one issue I just found though and that's the holes for the sample clips to screw into.  They're too loose.  M3 screws go right in and don't bite into the material at all.  But the holes in the clips are too small for M4 screws and M4 screws won't fit into the mounting holes either.  All the other hole sizes seem correct just these are way loose for me.

Only other feedback so far is that the docs haven't been updated to mention the nut traps for mounting the dovetail to the main body.  Nice addition though!  Also the estimated print times in the docs seem quite a bit off.  The v5.2 main body (with motor mounts since I have a bunch of 28byj steppers laying around) on my Prusa MK3 with prusa's default 0.2mm settings took 10 hours which is about double what the docs estimate.

rwb27, 2019-02-01:
Hi @jhitesma thanks for getting in touch - clearly I should have tested out those holes on more printers before I pushed them out!  they should self tap nicely with M3 screws, and it's odd that we get different results with the same printer!  I made a test object at some point to get the size of those holes right, I will see if I can find it as it would be interesting to see what settings work for you.

rwb27, 2019-02-01:
The nut traps for the dovetail are intended to be optional by the way, which is why they're not in the docs; the holes should be M3 "self tapping" triangles, but I guess those turned out too loose as well.

I would be curious to know whether the holes in the motor lugs are the right size - they should self tap with M4 screws.

Lastly, the print times in there are probably off because I put them in when I was pushing the printer to go faster (I might even have been using an 0.6mm nozzle).  10 hours is about what I'd expect with 0.2mm layers, I often use 0.3 though, and that prints fine too.

jhitesma, 2019-02-01:
The motor lug holes self tap with M4's just fine.  The dovetail also threaded with m3's but did seem a bit loose so I was glad the nuts were there.  Same with the holes in the Pi housing base - they self tapped with m3's just fine for me.  

[image]

Did some initial tests with it last night after I opened the issue and really happy with it so far, still have to wire up an illumination LED and without the O-rings adjustments are a bit limited but I'm really impressed by what the pi cam optics and your design are capable of so far.

[image]

Thanks so much for sharing your design!

jhitesma, 2019-02-04:
One other thing I noticed and had forgot about but remembered last night as I was falling asleep.

I didn't have to drill out the actuator holes even though I saw there was a drill guide now included.  The M3 screws were a very easy loose fit with no drilling.  Not sure if that may be related to the sample clip holes being loose or not but figured it was worth mentioning.

rwb27, 2019-02-06:
Awesome!  Well done :)

The drilling jig isn't usually required - only when the holes come out too small (usually due to the printer overextruding a bit).  If your holes are, on the whole, coming out a bit large, I would have been quite surprised if you'd needed to drill them.

jhitesma, 2019-02-07:
Scope is working great.  I took a look through the code and don't see anything that should cause the holes in the stage to be any larger than any of the other m3 holes.  Yet for some reason all the others were able to self-tap with no issues for me so this is really perplexing.  All I can think is that since the stage is essentially printed on top of a bridge maybe something in the printing process caused them to come out slightly distorted due to the "shaky foundation".  

Really impressed with it overall.  I'm just using a quick and dirty python script to stream the video out right now and adjusting things manually since I haven't wired up the steppers yet and am running the pi headless.  

Here's a quick screencap of testing it on a commercial slide of a pine stem:
https://photos.app.goo.gl/4n7zXuKdUHVbYRRY8

Started experimenting with the openflexure_microscope control script but can't seem to bring up video yet - nothing happens when I hit 'v'.  I haven't looked at the code there yet but I'm guessing it may be because I'm using VNC to bring up a remote desktop, so if the video is just fed straight to the HDMI output I won't see it.

Kind of liking using it through a webpage like this though. The very slight delay is a bit of a bummer, but it's kind of neat having a web connected microscope :D  Letting my parents on the other side of the country and my daughter explore together is pretty cool 👍

rwb27, 2019-02-11:
Thanks for posting - that's awesome :)  I was going to check the code to see if those holes were accidentally larger, but you've beaten me to it.  Thanks!  I would expect the bottom of the stage to print a bit funny due to the bridging, but it should be sorted out by the time you get to the top so it does surprise me a bit that those holes are coming out bigger.

I've made a little test object (in the repository as well in e3ee8d967586593d7327f821c781200d8d9c3cf4) with differently sized holes.  If you fancied printing it and letting me know which holes tapped nicely, that would be really helpful.

Given that this is now a really nice build report, it might be worth re-raising the original issue about the holes, to publicise the form and [test piece, which is currently in a gist](https://gist.github.com/rwb27/9c3ac259831a2d4316a7ae65a9f460fc) because I can't upload it to an issue.

jhitesma, 2019-02-14:
I'll give the test piece a try tonight, I'm really perplexed by it as well.  The screw does seem to start to tap just before it bottoms out in those holes on the stage - but just for one or two threads so not enough to hold the clips.  (I tried longer screws to confirm I wasn't just using too short of screws - but they didn't bite any better.)

Want me to rename this as a build report?  Do you want to open a new issue dedicated to the holes or did you want me to do that?

jhitesma, 2019-02-16:
Just shared my first results on the test piece.  Everything from 2.6 to 3.2 was usable.  Though 3.2 was a little loose and 2.6 was a little tight.  

But...I need to do a few more tests.  I used a different brand of PLA and I accidentally sliced at 0.15mm instead of the 0.2 I used for the scope.  Will try with a few different brands of PLA and layer heights.

If I get time this weekend (3 day weekend for me so there's a decent chance I'll find time) I may try making a test piece that uses the actual stage from your .scad files but which is just the stage on some short feet.  So it would print a lot quicker than the hole scope but would let me see how the stage itself prints in real life.  

BTW - I really like the idea of the trylinders.  Just driving me crazy trying to figure out why the ones on the stage didn't work very well for me.

rwb27, 2019-02-18:
thanks - that is interesting.  For me, the biggest one that worked was 3.2 or 3.4, so it's really not that different.  Trying it out on the actual stage would be interesting.  I guess it can be worked around (e.g. by drilling out the hole and putting a nut underneath) but that's not very satisfying, and I am a bit mystified.  It would be interesting to see if you can reproduce the issue in a stage-shaped test piece.  I guess just cropping out the relevant bit from an STL of the microscope might already do it...

rwb27, 2019-02-18:
Just for the record, the [line that makes the holes](https://github.com/rwb27/openflexure_microscope/blob/master/openscad/main_body.scad#L205) is definitely trying to make them the same as the others.  I know you checked that already, just wanted to give it a second pair of eyes...

rwb27, 2019-02-21:
Also, I checked a few of my printed bodies - I hadn't noticed before, but the trylinder holes in the stage are definitely looser.  Mine just about work, but I think I might just make them 10% smaller on the grounds that it clearly isn't just my printer!  I've got a body I printed on the Ultimaker somewhere that I should test as well.

jhitesma, 2019-02-21:
Good to know it's not just me then :D  I haven't had time to try and test just a stage yet but it's high on my priority list.  Very interesting that apparently it's consistent across printers - I can easily see loosing some precision printing on top of a bridge like that.  I just wouldn't have expected it to manifest like this.

rwb27, 2019-04-30:
The repository is [moving to GitLab](https://gitlab.com/openflexure/openflexure-microscope/), and this issue has been migrated.  I'll close all the issues here in due course, but am leaving notices on all the currently-open ones.  If you head over to the other repository, this issue will be updated there.

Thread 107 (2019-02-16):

rwb27/openflexure_microscope #107: not enough power to motors? maybe I need to power the driver PCB separately?

ctzurcanu, 2019-02-16:
When I try different values for x,y,z I noticed that for 500 the motors rotate. But for -500 they do not. When returning to 500, they work again.
Power is from the Arduino nano power that is into Rasp PI board.

rwb27, 2019-02-18:
Ah, yes - I always use separate motor power.  I think the v2 Sangaboard does have an unfortunate connection between the 5v pin on the Arduino and the 5v motor power - we have had issues with back-powering the Raspberry Pi through the USB line, you may want to think about cutting the trace that connects to the Arduino's 5v pin...

My usual method is to put screw terminals on the Sangaboard, and then wire a 5v Raspberry Pi into those, and then wire from the screw terminals into the Pi's micro USB power port (using the cut-off end of the cable).  If I'm being slightly nicer, I use a male-female micro USB lead, and cut it in the middle to expose the 5v and 0v lines, then do the same thing.  It's a bit of a bodge; the v3 Sangaboard has both micro USB power input and USB type A power output for the Pi, but it's currently not in the repo (I do periodically remind @sangavalerian to upload it).  It's surface-mount only though, and requires a 2 sided board with vias.  We're getting the first batch made by Seeed now.

rwb27, 2019-02-20:
I think you commented in the build report #102 that you used the power directly from the Pi (I guess the 0v and 5v GPIO pins?).  I've not usually done this as I was worried about blowing the polyfuse on the Pi, so it's interesting if that works for you...

ctzurcanu, 2019-02-20:
I figured that if Pi remains in server mode, it consumes only about 5% CPU. It should not draw a lot of juice. but I have not measured.
Yes. It is risky and I may take the power from the source, but I did not have sockets home now to use.
Maybe in 2-3 days, I will get to this too.

rwb27, 2019-04-30:
did you get this working in the end?  I think from your build report you might have done?  I should have added that my usual solution to having too few sockets is to make a custom power lead, with one micro-USB and another connector that I can plug directly in to the motor board.  One 10W Raspberry Pi PSU is usually sufficient, but this way avoids the polyfuse.

rwb27, 2019-04-30:
The repository is [moving to GitLab](https://gitlab.com/openflexure/openflexure-microscope/), and this issue has been migrated.  I'll close all the issues here in due course, but am leaving notices on all the currently-open ones.  If you head over to the other repository, this issue will be updated there.

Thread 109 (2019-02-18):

rwb27/openflexure_microscope #109: Whaat way to insert the lens

ctzurcanu, 2019-02-18:
at: http://rwb27.github.io/openflexure_microscope/docs/2a_basic_optics_module.html

Step 7: It is not clear which side of the lens should face inside the dark chamber.

rwb27, 2019-02-18:
thanks for flagging that up, I should definitely update the instructions.  The side that normally faces the camera sensor should face the sample, so the side that normally faces out (with the smaller window, and the four flanges that you used to unscrew it) should face down.

rwb27, 2019-02-27:
I just updated the text in step 7 and I think it's fairly clear (ca77ff84245f3d23c2e92ca1d59a6f1fd2a01a81) - I guess a picture showing the right and wrong way to orient the lens would be helpful though.

rwb27, 2019-04-30:
The repository is [moving to GitLab](https://gitlab.com/openflexure/openflexure-microscope/), and this issue has been migrated.  I'll close all the issues here in due course, but am leaving notices on all the currently-open ones.  If you head over to the other repository, this issue will be updated there.

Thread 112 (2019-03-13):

rwb27/openflexure_microscope #112: What lenses do I need to use a 10x NPL FLUOTAR Objective?

rwb27, 2019-03-13:
I want to acquire tiled fluorescence images of 'comet cell' assays, so don't need huge magnifications, and we use SYBR safe for green fluorescence.  I have an NPL FLUOTAR 10x objective available (0.3) from Leitz, and wonder for the optics parts, if that will be sufficient. However, is it the piece f40d16 or the f50d13 that would be the most appropriate to make?  It is clear that one is shorter than the other, of course...  (next step before printing - to see if our black filament is matt or shiny!) . Thanks!

_Originally posted by @rachelaronoff in https://github.com/rwb27/openflexure_microscope/issues/43#issuecomment-472307883_

rwb27, 2019-03-13:
Hi @rachelaronoff, you do need one extra lens to make it work properly; the design is meant to use a "finite conjugates" microscope objective, together with a secondary lens to shorten the distance to the sensor and adjust the image size to fit the Pi camera. The two pre-compiled options are:

    a 12.7mm diameter, 50mm focal length achromatic lens, e.g. ThorLabs AC127-050-A - fits f50d13
    a 16mm diameter, 40mm focal length lens, e.g. Comar 40 PC 16 (I think) - fits f40d16
    I reccommend the ThorLabs lens, it is slightly more expensive, but gives better quality images.

If you have an "infinity corrected" lens, you are lucky (these are generally more expensive and better quality) but it won't work properly with either of the options; you will still need one of the above lenses, but would need to compile a custom optics module. If that's the case, let me know and I'll compile one for you - it would be no bad thing to add this to the build script.

If you are not sure whether your objective is infinity corrected or finite conjugates, look at the writing on the side of it. If the number 160 appears anywhere, it is probably a standard finite-conjugates objective. If the infinity symbol is present, it's probably infinity corrected. Most RMS-threaded objectives (i.e. ones that will fit the plastic part) are finite conjugates. Modern infinity-corrected lenses tend to have larger threads.

Lastly, you can build the microscope without the additional lens. It will still produce images, but they will be of lower quality and the magnification will be different. I don't reccommend this, but it's possible it will work for your application.

closed 2019-03-13 by rwb27

MakerTobey, 2019-03-14:
Reference to follow up question:
https://github.com/rwb27/openflexure_microscope/issues/43#issuecomment-472930303 
And response:
https://github.com/rwb27/openflexure_microscope/issues/43#issuecomment-472931448

I guess this is where I start using OpenSCAD :-)

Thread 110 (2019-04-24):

### ISSUE TITLE
No instructions about sample riser

### ISSUE THREAD

**Issue by jtc42** [rwb27/openflexure_microscope#110]

**Comment by sctv** [comment]
hi @jtc42 
Can you expand the issue a bit.  
What do you want to know about the sample riser?
Are you using it in a build of an open flexure microscope?  
Cheers,
Brian

**Comment by rwb27** [comment]
It's now mentioned in the final assembly page in the instructions, as of 1409567aa4b7cada70bdada6e3233dbf6cbc6208

The sample riser simply raises the sample up 10mm, allowing the use of a longer microscope objective - I now mostly use better-corrected, 45mm parfocal objectives (the smaller, cheaper ones are 35mm parfocal).

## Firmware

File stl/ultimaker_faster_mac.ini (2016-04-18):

[profile]
layer_height = 0.2
wall_thickness = 0.8
retraction_enable = True
solid_layer_thickness = 0.8
fill_density = 33
print_speed = 75
print_temperature = 210
print_temperature2 = 0
print_temperature3 = 0
print_temperature4 = 0
print_temperature5 = 0
print_bed_temperature = 70
support = None
platform_adhesion = Brim
support_dual_extrusion = Both
wipe_tower = False
wipe_tower_volume = 15
ooze_shield = False
filament_diameter = 2.85
filament_diameter2 = 0
filament_diameter3 = 0
filament_diameter4 = 0
filament_diameter5 = 0
filament_flow = 100.0
nozzle_size = 0.4
retraction_speed = 40.0
retraction_amount = 4.5
retraction_dual_amount = 16.5
retraction_min_travel = 1.5
retraction_combing = All
retraction_minimal_extrusion = 0.02
retraction_hop = 0.0
bottom_thickness = 0.3
layer0_width_factor = 120
object_sink = 0.0
overlap_dual = 0.15
travel_speed = 150.0
bottom_layer_speed = 20
infill_speed = 80
solidarea_speed = 30
inset0_speed = 30
insetx_speed = 60
cool_min_layer_time = 5
fan_enabled = True
skirt_line_count = 1
skirt_gap = 3.0
skirt_minimal_length = 150.0
fan_full_height = 0.5
fan_speed = 100
fan_speed_max = 100
cool_min_feedrate = 10
cool_head_lift = False
solid_top = True
solid_bottom = True
fill_overlap = 15
perimeter_before_infill = False
support_type = Lines
support_angle = 60
support_fill_rate = 15
support_xy_distance = 0.7
support_z_distance = 0.15
spiralize = False
simple_mode = False
brim_line_count = 20
raft_margin = 5.0
raft_line_spacing = 3.0
raft_base_thickness = 0.3
raft_base_linewidth = 1.0
raft_interface_thickness = 0.27
raft_interface_linewidth = 0.4
raft_airgap_all = 0.0
raft_airgap = 0.22
raft_surface_layers = 2
raft_surface_thickness = 0.27
raft_surface_linewidth = 0.4
fix_horrible_union_all_type_a = True
fix_horrible_union_all_type_b = False
fix_horrible_use_open_bits = False
fix_horrible_extensive_stitching = False
plugin_config = 
object_center_x = -1
object_center_y = -1

[alterations]
start.gcode = ;Sliced at: {day} {date} {time}
	;Basic settings: Layer height: {layer_height} Walls: {wall_thickness} Fill: {fill_density}
	;Print time: {print_time}
	;Filament used: {filament_amount}m {filament_weight}g
	;Filament cost: {filament_cost}
	;M190 S{print_bed_temperature} ;Uncomment to add your own bed temperature line
	;M109 S{print_temperature} ;Uncomment to add your own temperature line
	G21        ;metric values
	G90        ;absolute positioning
	M82        ;set extruder to absolute mode
	M107       ;start with the fan off
	G28 X0 Y0  ;move X/Y to min endstops
	G28 Z0     ;move Z to min endstops
	G1 Z15.0 F{travel_speed} ;move the platform down 15mm
	G92 E0                  ;zero the extruded length
	G1 F200 E3              ;extrude 3mm of feed stock
	G92 E0                  ;zero the extruded length again
	G1 F{travel_speed}
	;Put printing message on LCD screen
	M117 Printing...
end.gcode = ;End GCode
	M104 S0                     ;extruder heater off
	M140 S0                     ;heated bed heater off (if you have it)
	G91                                    ;relative positioning
	G1 E-1 F300                            ;retract the filament a bit before lifting the nozzle, to release some of the pressure
	G1 Z+0.5 E-5 X-20 Y-20 F{travel_speed} ;move Z up a bit and retract filament even more
	G28 X0 Y0                              ;move X/Y to min endstops, so the head is out of the way
	M84                         ;steppers off
	G90                         ;absolute positioning
	;{profile_string}
start2.gcode = ;Sliced at: {day} {date} {time}
	;Basic settings: Layer height: {layer_height} Walls: {wall_thickness} Fill: {fill_density}
	;Print time: {print_time}
	;Filament used: {filament_amount}m {filament_weight}g
	;Filament cost: {filament_cost}
	;M190 S{print_bed_temperature} ;Uncomment to add your own bed temperature line
	;M104 S{print_temperature} ;Uncomment to add your own temperature line
	;M109 T1 S{print_temperature2} ;Uncomment to add your own temperature line
	;M109 T0 S{print_temperature} ;Uncomment to add your own temperature line
	G21        ;metric values
	G90        ;absolute positioning
	M107       ;start with the fan off
	G28 X0 Y0  ;move X/Y to min endstops
	G28 Z0     ;move Z to min endstops
	G1 Z15.0 F{travel_speed} ;move the platform down 15mm
	T1                      ;Switch to the 2nd extruder
	G92 E0                  ;zero the extruded length
	G1 F200 E10             ;extrude 10mm of feed stock
	G92 E0                  ;zero the extruded length again
	G1 F200 E-{retraction_dual_amount}
	T0                      ;Switch to the first extruder
	G92 E0                  ;zero the extruded length
	G1 F200 E10             ;extrude 10mm of feed stock
	G92 E0                  ;zero the extruded length again
	G1 F{travel_speed}
	;Put printing message on LCD screen
	M117 Printing...
end2.gcode = ;End GCode
	M104 T0 S0                     ;extruder heater off
	M104 T1 S0                     ;extruder heater off
	M140 S0                     ;heated bed heater off (if you have it)
	G91                                    ;relative positioning
	G1 E-1 F300                            ;retract the filament a bit before lifting the nozzle, to release some of the pressure
	G1 Z+0.5 E-5 X-20 Y-20 F{travel_speed} ;move Z up a bit and retract filament even more
	G28 X0 Y0                              ;move X/Y to min endstops, so the head is out of the way
	M84                         ;steppers off
	G90                         ;absolute positioning
	;{profile_string}
start3.gcode = ;Sliced at: {day} {date} {time}
	;Basic settings: Layer height: {layer_height} Walls: {wall_thickness} Fill: {fill_density}
	;Print time: {print_time}
	;Filament used: {filament_amount}m {filament_weight}g
	;Filament cost: {filament_cost}
	;M190 S{print_bed_temperature} ;Uncomment to add your own bed temperature line
	;M104 S{print_temperature} ;Uncomment to add your own temperature line
	;M109 T1 S{print_temperature2} ;Uncomment to add your own temperature line
	;M109 T0 S{print_temperature} ;Uncomment to add your own temperature line
	G21        ;metric values
	G90        ;absolute positioning
	M107       ;start with the fan off
	G28 X0 Y0  ;move X/Y to min endstops
	G28 Z0     ;move Z to min endstops
	G1 Z15.0 F{travel_speed} ;move the platform down 15mm
	T2                      ;Switch to the 3rd extruder
	G92 E0                  ;zero the extruded length
	G1 F200 E10             ;extrude 10mm of feed stock
	G92 E0                  ;zero the extruded length again
	G1 F200 E-{retraction_dual_amount}
	T1                      ;Switch to the 2nd extruder
	G92 E0                  ;zero the extruded length
	G1 F200 E10             ;extrude 10mm of feed stock
	G92 E0                  ;zero the extruded length again
	G1 F200 E-{retraction_dual_amount}
	T0                      ;Switch to the first extruder
	G92 E0                  ;zero the extruded length
	G1 F200 E10             ;extrude 10mm of feed stock
	G92 E0                  ;zero the extruded length again
	G1 F{travel_speed}
	;Put printing message on LCD screen
	M117 Printing...
end3.gcode = ;End GCode
	M104 T0 S0                     ;extruder heater off
	M104 T1 S0                     ;extruder heater off
	M104 T2 S0                     ;extruder heater off
	M140 S0                     ;heated bed heater off (if you have it)
	G91                                    ;relative positioning
	G1 E-1 F300                            ;retract the filament a bit before lifting the nozzle, to release some of the pressure
	G1 Z+0.5 E-5 X-20 Y-20 F{travel_speed} ;move Z up a bit and retract filament even more
	G28 X0 Y0                              ;move X/Y to min endstops, so the head is out of the way
	M84                         ;steppers off
	G90                         ;absolute positioning
	;{profile_string}
start4.gcode = ;Sliced at: {day} {date} {time}
	;Basic settings: Layer height: {layer_height} Walls: {wall_thickness} Fill: {fill_density}
	;Print time: {print_time}
	;Filament used: {filament_amount}m {filament_weight}g
	;Filament cost: {filament_cost}
	;M190 S{print_bed_temperature} ;Uncomment to add your own bed temperature line
	;M104 S{print_temperature} ;Uncomment to add your own temperature line
	;M109 T2 S{print_temperature2} ;Uncomment to add your own temperature line
	;M109 T1 S{print_temperature2} ;Uncomment to add your own temperature line
	;M109 T0 S{print_temperature} ;Uncomment to add your own temperature line
	G21        ;metric values
	G90        ;absolute positioning
	M107       ;start with the fan off
	G28 X0 Y0  ;move X/Y to min endstops
	G28 Z0     ;move Z to min endstops
	G1 Z15.0 F{travel_speed} ;move the platform down 15mm
	T3                      ;Switch to the 4th extruder
	G92 E0                  ;zero the extruded length
	G1 F200 E10             ;extrude 10mm of feed stock
	G92 E0                  ;zero the extruded length again
	G1 F200 E-{retraction_dual_amount}
	T2                      ;Switch to the 3rd extruder
	G92 E0                  ;zero the extruded length
	G1 F200 E10             ;extrude 10mm of feed stock
	G92 E0                  ;zero the extruded length again
	G1 F200 E-{retraction_dual_amount}
	T1                      ;Switch to the 2nd extruder
	G92 E0                  ;zero the extruded length
	G1 F200 E10             ;extrude 10mm of feed stock
	G92 E0                  ;zero the extruded length again
	G1 F200 E-{retraction_dual_amount}
	T0                      ;Switch to the first extruder
	G92 E0                  ;zero the extruded length
	G1 F200 E10             ;extrude 10mm of feed stock
	G92 E0                  ;zero the extruded length again
	G1 F{travel_speed}
	;Put printing message on LCD screen
	M117 Printing...
end4.gcode = ;End GCode
	M104 T0 S0                     ;extruder heater off
	M104 T1 S0                     ;extruder heater off
	M104 T2 S0                     ;extruder heater off
	M104 T3 S0                     ;extruder heater off
	M140 S0                     ;heated bed heater off (if you have it)
	G91                                    ;relative positioning
	G1 E-1 F300                            ;retract the filament a bit before lifting the nozzle, to release some of the pressure
	G1 Z+0.5 E-5 X-20 Y-20 F{travel_speed} ;move Z up a bit and retract filament even more
	G28 X0 Y0                              ;move X/Y to min endstops, so the head is out of the way
	M84                         ;steppers off
	G90                         ;absolute positioning
	;{profile_string}
support_start.gcode = 
support_end.gcode = 
cool_start.gcode = 
cool_end.gcode = 
replace.csv = 
preswitchextruder.gcode = ;Switch between the current extruder and the next extruder, when printing with multiple extruders.
	;This code is added before the T(n)
postswitchextruder.gcode = ;Switch between the current extruder and the next extruder, when printing with multiple extruders.
	;This code is added after the T(n)

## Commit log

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2016-03-23 Removed illumination column and replaced with dovetail
    [dovetail.scad, illumination_and_rear_foot.scad, main_body.scad]
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2016-04-06 Unified RMS and picam models
    Everything now compiles from the same (slightly monster) file. Probably
    need to fix the tube lens placement though.
    [optics_all_in_one.scad]
2016-04-06 Fixed RMS tube lens position and consolidated everything.
    [RMS_camera_mount.scad, optics.scad, optics_all_in_one_6mm_achromat.scad, optics_all_in_one_6mm_achromat_2.scad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]
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2016-04-19 Redesigned illumination to fit with dovetail the other way around.
    [12mm_dovetail.stl, dovetail.scad, dovetail_clip_y_test.stl, illumination_and_rear_foot.scad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]
2016-04-23 Improved dovetail and illumination
    It’s now got an endstop, and it’s thick where it needs to be but not
    everywhere else (prints faster and more clearance for cables).
    [4x_body.scad, dovetail.scad, illumination_and_rear_foot.scad, illumination_and_rear_foot_standard_stage.stl]
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2016-05-05 Fixed slash in include
    forward slash it turns out is platform-independent. Backslash confuses
    mac/linux machines.
    [gears.scad]
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2016-05-31 Fixed gitignore to allow STL files in docs
    [all_parts_picam1.stl, all_parts_picam2.stl, bed1_tall_picam2.stl, bed2_shallow.stl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]
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2016-06-20 Joined legs correctly onto main body.
    The bottom flexures weren’t actually part of the main body - there was
    a zero width gap between the flexures and the wall. This is now fixed.
    Also, I added slight indents either side of where the flexures join the
    wall to ensure it’s properly retained.
    [main_body.scad, microscope_parameters.scad]
2016-06-21 Another fix to the attachment of legs to body
    The sloping-in wall round the microscope body meant the flexures
    weren’t attaching (on some printers/slicers) - I’ve now made them go
    further in to the body, so they connect properly.
    [main_body.scad]
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2016-09-26 Thinned the bottom of the objective clip dovetail
    I'd inadvertently added 0.5+d to the thickness of the dovetail clip for
    the objective. That made it hard to clip in, and caused trouble when it
    broke, as it often did. The new, thinner bottom should be stretchier
    and easier to snip off if desired. Need to recompile the STL
    [main_body.scad]
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2016-10-28 variable led_r went nowhere, fixed
    at the top of the file, the variable led_r did not, as labeled, change
    the diameter of the LED holder. Also, while labeled ‘r’ it actually
    required a diameter-based input.
    I changed the variable to led_d and inserted it into the equations on
    lines 93 and 94.
    [illumination_and_rear_foot.scad, illumination_and_rear_foot_5mmLED_L65.stl]
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2016-12-12 added shift parameter to move around the condenser
    With everything in the "perfect" position, the condenser seemed to be
    about 2mm too far towards the Z nut. I've shifted it back, but I'm
    worried that's a tolerance issue rather than a static shift...
    [illumination_and_rear_foot.scad]
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2017-01-16 Rebuilt vanilla body to fix leg attachment issue
    [microscope_parameters.scad]
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2017-02-08 tightened nut trap and strengthened hooks
    Tweaks to geometry of the actuator column, to make the nut fit more
    snugly and make the hooks for elastic bands stronger.
    [compact_nut_seat.scad]
2017-02-08 Bug fix and trylinder gripper for pi lens optics
    Added a new (untested) optics module for the pi lens, using a
    "trylinder" gripper to avoid tape. Also fixed a bug introduced by
    fluorescence that caused non-fluorescence optics modules to fail.
    [optics.scad]
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2017-02-08 Fixed issues with feet
    The bottom of the feet is a simple shape - an oval outline with a
    section filled in in the middle. This should have a break for the
    elastic band, but it's missing on the tilted feet; I've now fixed this.
    [compact_nut_seat.scad, feet.scad, microscope_parameters.scad]
2017-02-09 Fixed feet
    By introducing nut_w I screwed up the feet... now fixed.
    [compact_nut_seat.scad, feet.scad, feet.stl, utilities.scad]
2017-02-09 Tightened nut slots a bit more
    [actuator_column.stl, compact_nut_seat.scad, microscope_parameters.scad]
2017-02-10 Tightened nut seat and recompiled
    it's too tight now!!
    [compact_nut_seat.scad, gears.scad, gears.stl, microscope_parameters.scad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]
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2017-02-17 fixed some bugs in the wall
    [compact_nut_seat.scad, main_body.scad, microscope_parameters.scad]
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2017-02-22 Fixed the screw shaft so it's long enough.
    I previously shortened the screw shaft inside the column - unfortunately
    I shortened it too much. I've now made it longer, but tapered the end
    for strength. The STL files are not updated so I deleted them.
    [compact_nut_seat.scad, nut_and_band_tool.stl]
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2017-03-01 Loosened the fit of the assembly tools
    [actuator_assembly_tools.scad, actuator_assembly_tools.stl]
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2017-03-02 Fixed a bug that broke the stage legs
    The flexure bridges that support the stage were failing - turns out I
    hadn't quite joined them on properly. This is now fixed.
    [main_body.scad, microscope_parameters.scad]
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2017-03-03 Modified elastic band tool
    The tool is now stronger and narrower - but it still doesn't fit through
    the foot very well, and I still managed to knock off one of the lugs
    from the band hook on the actuator column.
    [actuator_assembly_tools.scad, compact_nut_seat.scad]
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2017-03-17 Another design for adjustable illumination.
    I've put the adjustment in a slip plate now; needs less hardware, and
    probably prints better. It also comes off for transport. Only downside
    is it relies on the clip staying good; maybe I could add a screw in case
    the clip gets loose.
    [illumination_and_rear_foot.scad, illumination_and_rear_foot_ls65_condenser.stl, main_body.scad, optics.scad]
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2017-03-17 Better fit for illumination LED
    Using a feathered hole for the LED allows a tight fit with tolerance for
    slightly off-size LEDs.
    [condenser_lens_tool.scad, condenser_lens_tool.stl, illumination_and_rear_foot.scad, illumination_and_rear_foot_condenseronly.stl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]
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2017-04-06 Added a screw-in mount for the pi camera
    The push fit is problematic, particularly with v2 of the camera. This
    simpler design just screws on the camera module with two M2 screws.
    [microscope_parameters.scad, optics.scad, optics_picam2_screwin.stl, picam_2_screw_on.scad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]
2017-04-06 Fixed illumination for SS version
    The SS version was compiling a 65mm high illumination. Should now be
    fixed.
    [illumination_and_rear_foot.scad]
2017-04-06 Fixed illumination so it's the right height
    Illumination was set to 65mm stage height as a hard-coded constant. Now
    uses the value from microscope_parameters.
    [illumination_and_rear_foot.scad]
2017-04-06 Improved band clearance on insertion tools
    The band insertion tool now has a notch to clear the elastic band in its
    inserted position (i.e. when it's coming through the channel in the
    foot). Before, the prongs at the end were joined together in the
    middle, and this would jam on the bands.
    [actuator_assembly_tools.scad, actuator_assembly_tools.stl]
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2017-04-06 Added notched STL of actuator tools
    In case the screw-tightening feature is still useful, I've added an STL
    to do that.
    [actuator_assembly_tools_notched.stl]
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2017-04-06 Fixed illumination (again)
    Illumination is now the right height!
    [illumination_and_back_foot_adj_LS65.stl, illumination_and_back_foot_adj_SS.stl, illumination_and_back_foot_condenser_LS65.stl, illumination_and_back_foot_conde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]
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2017-04-27 Updated the illumination files
    The SS illumination was tall - now fixed.
    [illumination_and_back_foot_adj_LS65.stl, illumination_and_back_foot_adj_SS.stl, illumination_and_back_foot_condenser_LS65.stl, illumination_and_back_foot_conde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]
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2017-06-05 Corrected lens-to-sensor distance in RMS optics
    I did some testing and noticed that the distance from the lens to the
    sensor was wrong in the RMS optics module. This will partly be because
    the Pi camera sensor is now no longer in the plane of the board (it's
    raised up by the foam pad under the camera). I've added a function to
    the camera files that returns how high the sensor is, to allow it to be
    correct for different cameras.
    [C270_mount.scad, optics.scad, optics_picam2_rms.stl, optics_rms_t31_d10_s69_c270.stl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]
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2017-06-06 removed weak point at blade anchor
    The slot to allow clearance for the hook is now tapered, which should
    help keep the blades strong by elminating stress buildup at the anchor
    [actuator_assembly_tools.scad, band_tool.stl]
2017-06-06 double-ended band tool
    The double-ended band tool pushes both ends of the O ring in
    simultaneously, eliminating the over-stretching issue that tends to snap
    bands (I hope).
    [actuator_assembly_tools.scad, band_tool_double_ended.stl]
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
